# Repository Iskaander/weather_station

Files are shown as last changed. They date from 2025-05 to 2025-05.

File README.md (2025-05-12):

# weather_station

A little weather station I built to go with my spectrometers.

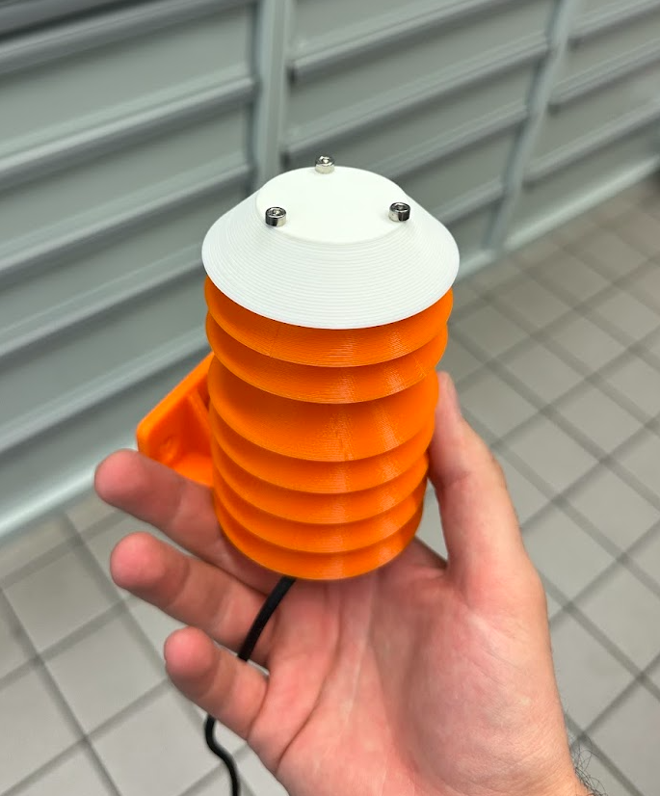
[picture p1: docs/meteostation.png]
The built station

*(The finished weather station setup)*

This is a project for a small, reasonably cheap weather station. The main idea was to have something to measure atmospheric conditions (especially pressure and temperature) when running laser spectrometers. Those readings are complimentary to the measurements of greenhouse gases. But I thought it would be also nice to track humidity and CO2 levels.

I sometimes do the measurements in different places, so I included a GPS receiver. This gives me location, altitude, and time, which I can then use to blend my data with weather models like ERA5.

There are probably off-the-shelf weather stations, but I wanted a specific set of sensors, aiming for good precision for each measurement.
UPD: This is a standard P/T/H station for EU measurements with COCCON: PCE-THB 40 for 300 eur
https://www.pce-instruments.com/deutsch/messtechnik/messgeraete-fuer-alle-parameter/temperatur-datenlogger-temperaturlogger-pce-instruments-temperatur-datenlogger-pce-thb-40-det_3711876.htm

## What's Inside & Cost

Here's the parts list. Total comes out to around $153 USD:

1.  **GPS:** Adafruit ULTIMATE GPS PA1616S - $30
2.  **Pressure:** MIKROE-5921 BMP585 board - $23 (This sensor is new and most precise +-6Pa relative and +-50 Pa absolute accuracy)
3.  **CO2:** Sensirion SCD30 - $33 (Stable NDIR CO2 sensor +-30.0 ppm)
4.  **Temp/Humidity:** Sensirion SHT85 - $28 (Sensirion is known for good accuracy 1.5	%RH accruacy and 0.1 degC for temperature)
5.  **MCU:** Teensy 4.1 - $39 (Versatile and fast up to 600mhz)

An SD card isn't strictly necessary, but if you want to log data, a 16GB one formatted to FAT32 works fine.

## Putting it Together

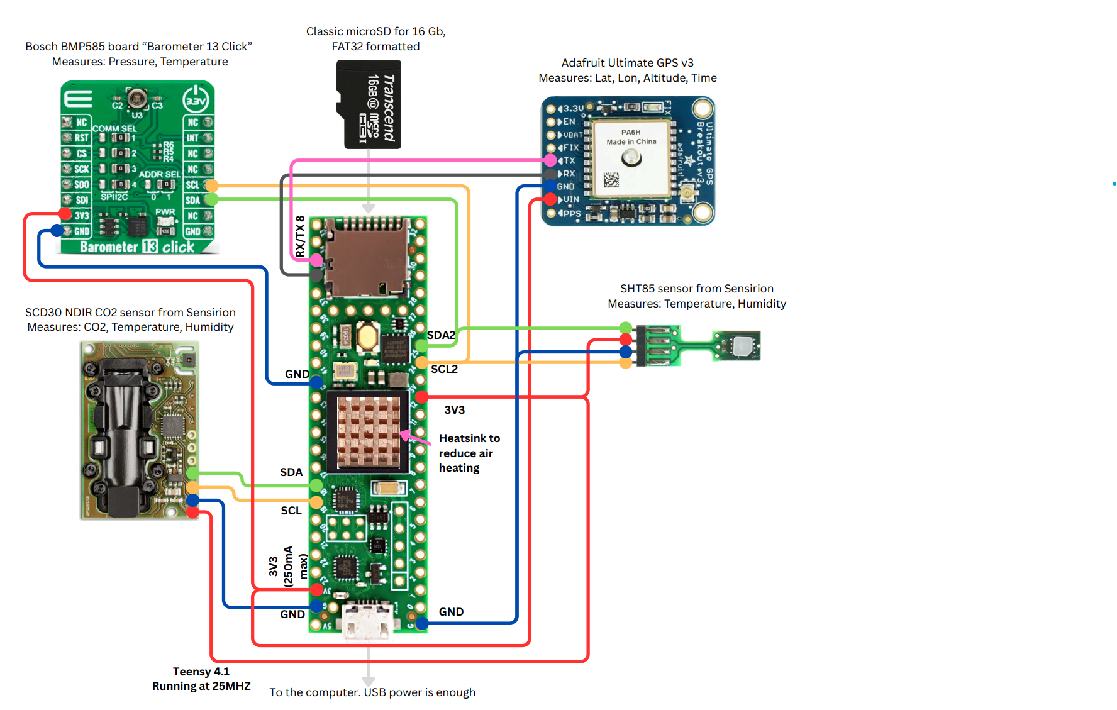
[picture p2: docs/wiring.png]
Wiring diagram

*(How things are wired up)*

I just soldered everything onto a perfboard. No PCB design for this one, as I didn't have the time, and perfboarding it took about a day of wiring and soldering.

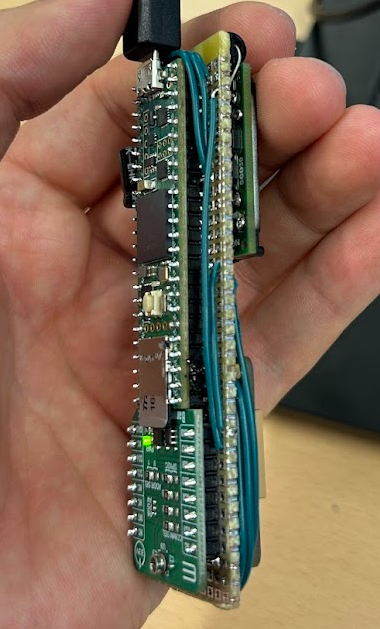
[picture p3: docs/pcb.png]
The PCB

*(The soldered parts)*

Try to put SHT85 sensor away from the heat sources - as this is your precise measurement of air temperature.

The 3D printed enclosure files are great, but you have to stop mid print to insert m3 nuts for the top part. The sensors and Teensy fit nicely. You'll likely need to print 9 of the "middle sections" to get enough height to cover the board properly. You also need m3 rods to connect the parts.

## The Code

 Most of the code was written by Gemini 2.5 Pro Preview (Google). It works... But I am in the middle of my PhD so there is no time for a more readable version.

### Libraries You'll Need:

They are included in the repo, but most of them could be installed via Arudino interface in IDE. Also there was no library for Bosch sensor, so I took parts of the code from this website https://www.electroniclinic.com/bosch-bmp585-barometric-pressure-sensor-with-arduino/

### Getting it Running:
1.  Make sure you have the Arduino IDE and Teens set up.
2.  Install the libraries listed above.
3.  Grab the code from this repository.
4.  Open the main `.ino` file, select Teensy 4.1 as your board, and upload. I also recommend setting teensy CPU speed to 24Mhz in "tools" menu but this is already done.

## How it Works (Briefly)

It checks for SD card, communicates to the sensors and then starts logging data and sending it to the UART. Logging interval is 1 second. After 12hours of logging it will make a new CSV on SD card. If something goes wrong the main LED will turn on. You can also monitor the status via serial interface in arduino. 

This is the CSV header:
"Log_Index,CPU_TempC,BMP_TempC,BMP_PressPa,CO2_ppm,SCD30_TempC,SCD30_Hum_%,SHT_TempC,SHT_Hum_%,GPS_Lat,GPS_Lon,GPS_Alt_m,GPS_Year,GPS_Month,GPS_Day,GPS_Hour,GPS_Min,GPS_Sec,GPS_MilliSec,GPS_Fix,BMP_Health,SCD30_Health,SHT_Health"

Field Descriptions:

- **Log_Index**: For-loop cycle count.
- **CPU_TempC**: Temperature of the Teensy core in °C.
- **BMP_TempC**: Temperature from the BMP585 sensor in °C.
- **BMP_PressPa**: Pressure from the BMP585 sensor in Pascals (Pa).
- **CO2_ppm**: CO2 concentration in ppm from the SCD30 sensor.
- **SCD30_TempC**: Temperature from the SCD30 sensor in °C.
- **SCD30_Hum_%**: Humidity from the SCD30 sensor in %.
- **SHT_TempC**: Temperature from the SHT85 sensor in °C (most precise air temperature).
- **SHT_Hum_%**: Humidity from the SHT85 sensor in % (most precise air humidity).
- **GPS_Lat**, **GPS_Lon**: Coordinates in decimal degrees.
- **GPS_Alt_m**: Altitude above sea level in meters.
- **GPS_Year**, **GPS_Month**, **GPS_Day**, **GPS_Hour**, **GPS_Min**, **GPS_Sec**: Time from GPS.
- **GPS_MilliSec**: Milliseconds from GPS (currently always 0).
- **GPS_Fix**: 1 if GPS has a fix, 0 otherwise.
- **BMP_Health**: 1 if BMP585 is healthy, 0 otherwise.
- **SCD30_Health**: 1 if SCD30 is healthy, 0 otherwise.
- **SHT_Health**: 1 if SHT85 is healthy, 0 otherwise.

## Some results

Here are measurements for the weekend

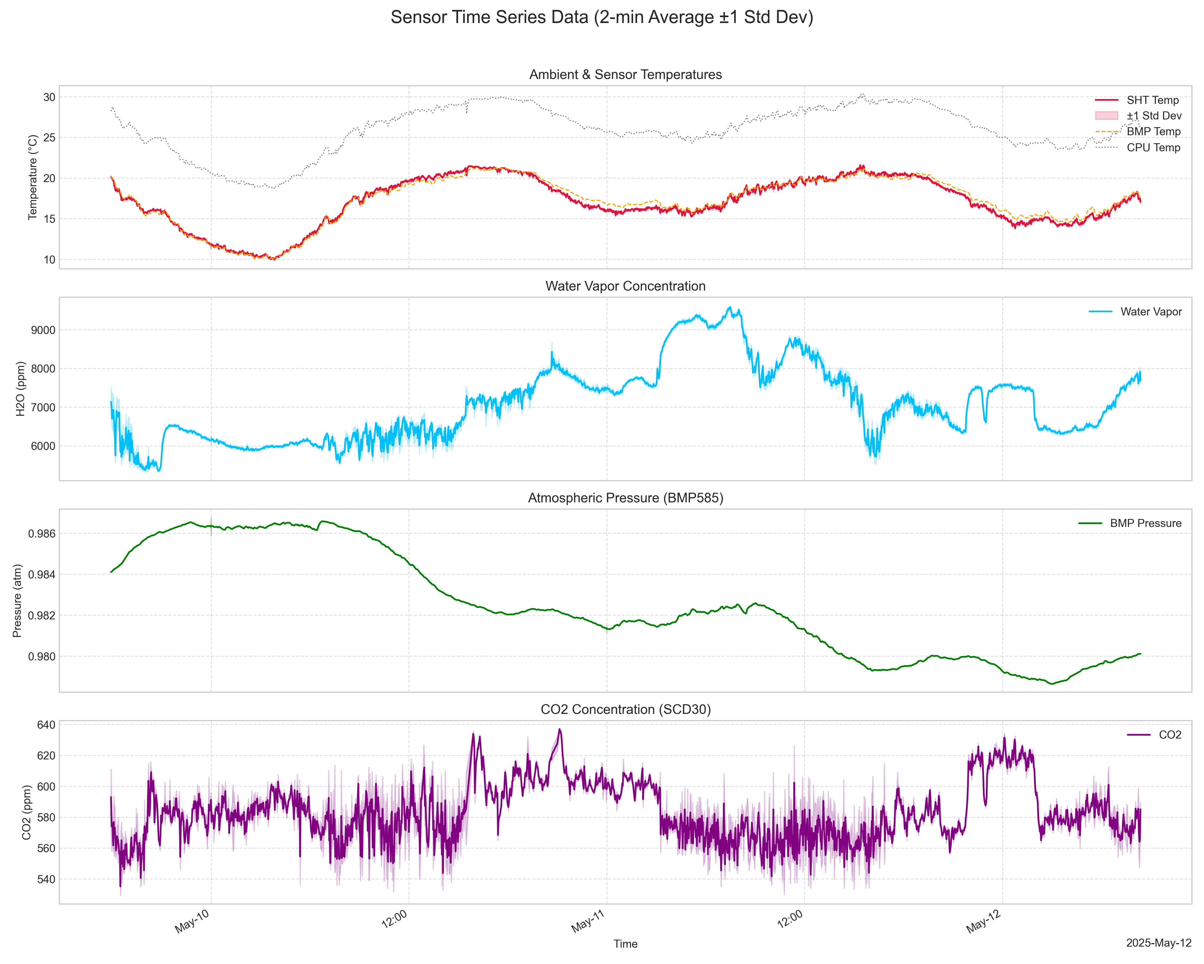
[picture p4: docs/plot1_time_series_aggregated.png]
2 day measurements

*(Measurements during 2 days in the shade in the city)*

And here is a comparison between different sensors

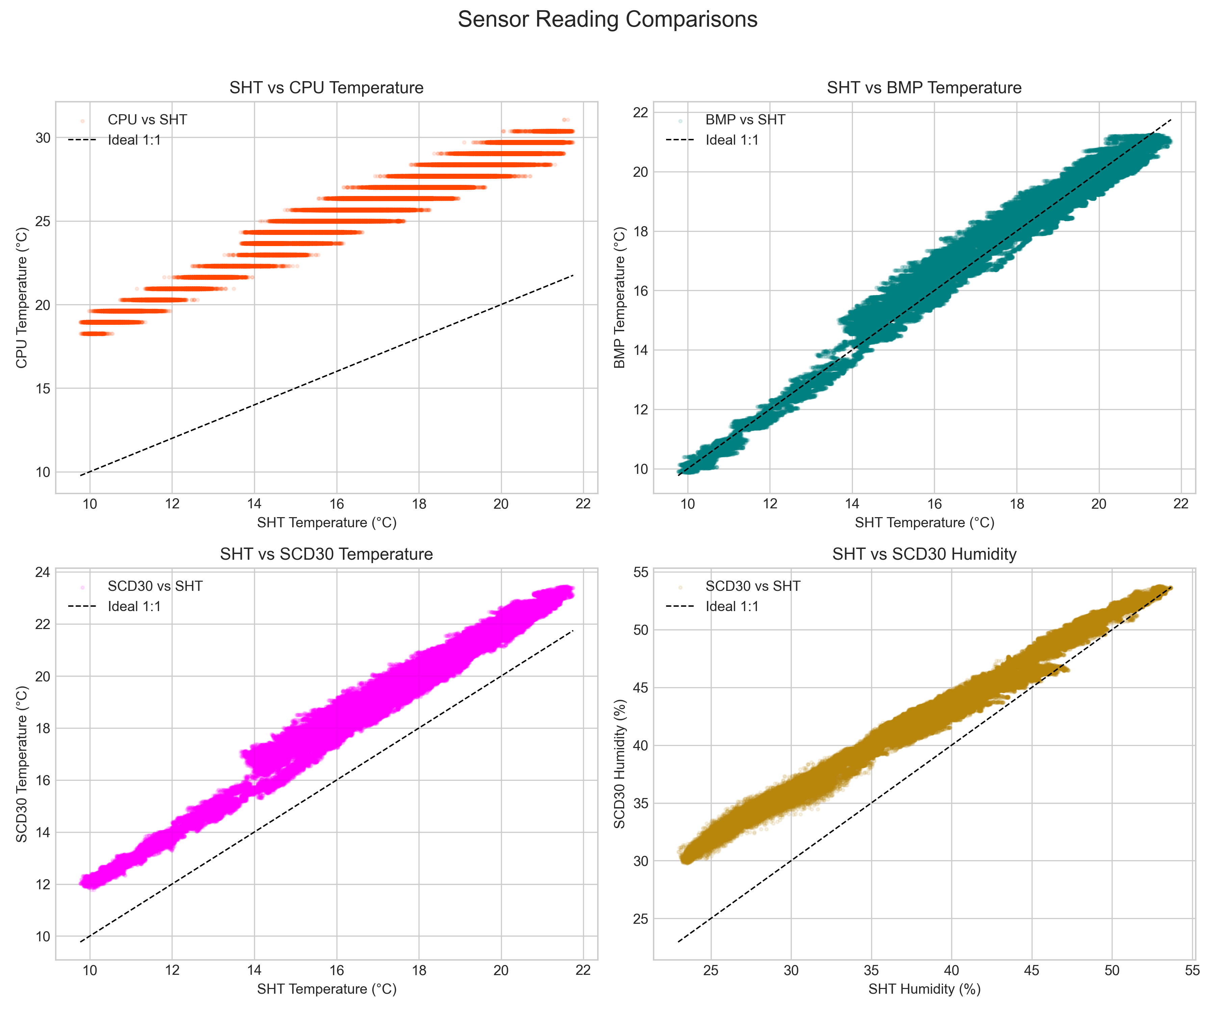
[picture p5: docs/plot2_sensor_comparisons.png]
Comparison

*(cross-comparison between sensors on the weather station)*

## Future tasks

1. Write visualisation from csv in Python
2. Write visualisation in real time in LabView
3. Write SD reading directly from Arduino
4. Fix GPS_MilliSec always = 0
5. Add MTP support to copy files from SD card directly

## Licensing

The code in this project is licensed under the MIT License - see the `LICENSE` file for details.

1.  **3D models:**
    *   The 3D models included in the `/3d_models` directory are licensed under the (CC BY 4.0).
    *   Source: https://www.printables.com/model/73421-radiation-shields-for-diy-weather-station
2.  **Adafruit GPS Library:**
    *   Licensed under the [BSD 3-Clause License]. The full license text is included with the library files.
    *   Source: https://github.com/adafruit/Adafruit_GPS?tab=License-1-ov-file#readme
3.  **Arduino-sht Library:**
    *   Licensed under the [BSD 3-Clause License]. The full license text is included with the library files.
    *   Source: https://github.com/Sensirion/arduino-sht?tab=BSD-3-Clause-1-ov-file#readme
4.  **InternalTemperature Library:**
    *   No license was provided in the repository at the time of creation of this document
    *   Source: https://github.com/LAtimes2/InternalTemperature
5.  **SD Library:**
    *   Licensed under the [GNU GENERAL PUBLIC LICENSE]. The full license text is included with the library files.
    *   Source: https://github.com/arduino-libraries/SD?tab=GPL-3.0-1-ov-file#readme
6.  **SparkFun_BMP581_Arduino_Library Library:**
    *   Licensed under the [MIT License]. The full license text is included with the library files.
    *   Source: https://github.com/sparkfun/SparkFun_BMP581_Arduino_Library?tab=License-1-ov-file#readme
7.  **SparkFun_SCD30_Arduino_Library Library:**
    *   Licensed under the [MIT License]. The full license text is included with the library files.
    *   Source: https://github.com/sparkfun/SparkFun_SCD30_Arduino_Library?tab=License-1-ov-file#readme
8.  **WDT_T4 Library:**
    *   Licensed under the [MIT License]. The full license text is included with the library files.
    *   Source: https://github.com/tonton81/WDT_T4?tab=MIT-1-ov-file#readme
9.  **BMP585 code:**
    *   No License was visible on that page at the time of writing this document
    *   Source: https://www.electroniclinic.com/bosch-bmp585-barometric-pressure-sensor-with-arduino/

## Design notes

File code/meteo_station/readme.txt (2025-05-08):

1. Set teensy CPU clock speed to 150 MHz in Arduino IDE "Tools" section.

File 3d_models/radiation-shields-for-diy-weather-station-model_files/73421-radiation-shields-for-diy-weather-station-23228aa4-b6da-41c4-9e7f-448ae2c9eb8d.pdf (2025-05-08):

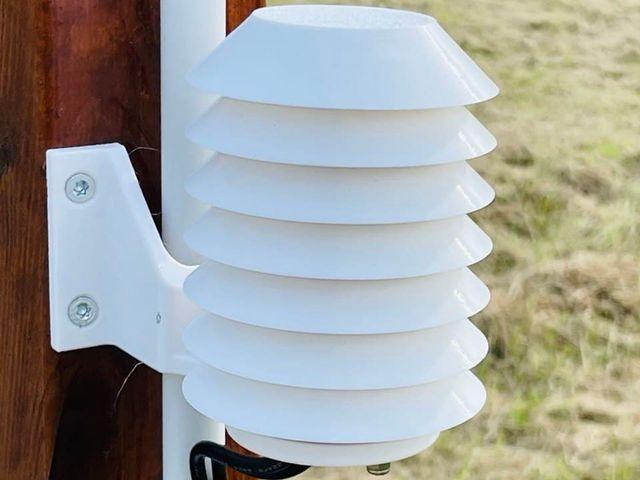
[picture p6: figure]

5.50 hrs

4 pcs

f

0.20 mm

k

0.40 mm

h

PET

51 g

d

Prusa MINI /

MINI+

## Summary

Universal radiation shields for various environmental sensors such as

temperature, air pressure or humidity

Hobby & Makers (https://www.printables.com/model?categoryId=48) | > | Other Ideas (https://www.printables.com/model?categoryId=82)

A universal radiation shield for various environmental sensors such as

temperature, air pressure or humidity. It is recommended to print the

radiation shield from PETG or another UV stable material.

## Print instructions

Parts

2x Stainless Steel Threaded Rod - 250mm M3 (https://s.click.aliexpress.com/e/_A2AYts)

3x Stainless Steel Washer - M3 (https://s.click.aliexpress.com/e/_9G1K2u)

6x Stainless Steel Hexagon Nuts - M3 (https://s.click.aliexpress.com/e/_AZAjvM) foorschtbar (https://www.printables.com/social/97471/about)

## Radiation shields

## for DIY weather

## station

VIEW IN BROWSER (https://www.printables.com/model/73421-radiation-shields-for-diy-weather-station)

updated 13. 9. 2022 | published 13. 9. 2022

•

•

•

# Model files

Assembly

Print one of the Bases (Normal, V2 or V3)

Print Top

Use 4 vertical perimeters

Pause while printing to insert nuts

Print Rings depending on your needs

Use 4 vertical perimeters

I printed six rings

Cut the threaded rods to your needs. Some tips:

The top hole is 6.8mm deep

Each ring needs 12mm

The base needs 12.5mm

Add some space at the end for the nuts and the washer

With six rings I shortened the threaded rods to 100mm

## Links

The links to AliExpress are advertising links. I would be happy if you use

this link, but of course you don't have to. I have linked exactly the offers

from which I have also bought and was satisfied with the supplier and the

goods. The products can of course be bought anywhere.

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
radiation_shield_base.stl

radiation_shield_top.stl

radiation_shield_ring.stl

radiation_shield_auxholder_v3-2.stl

## Print files

h PET | k 0.40 mm | f 0.20 mm | 0.89 hrs | 8 g | d Prusa MINI / MINI+
- Single Ring
h PET | k 0.40 mm | f 0.20 mm | 2.65 hrs | 26 g | d Prusa MINI / MINI+
- Three rings at once
h PET | k 0.40 mm | f 0.20 mm | 1.18 hrs | 12 g | d Prusa MINI / MINI+
h PET | k 0.40 mm | f 0.20 mm | 3.43 hrs | 31 g | d Prusa MINI / MINI+

radiation_shield_auxholder_v3-1.stl

radiation_shield_base_v2.stl

radiation_shield_base_v3-2.stl

radiation_shield_base_v3-1.stl

prusa_radiation_shield_ring_02mm_petg_mini_53m.gcode

prusa_radiation_shield_ring_02mm_petg_mini_2h39.gcode

prusa_radiation_shield_top_02mm_petg_mini_1h11m.gcode

prusa_radiation_shield_base_02mm_petg_mini_3h26.gcode

## License

This work is licensed under a

Creative Commons (4.0 International License)

Attribution (http://creativecommons.org/licenses/by/4.0/)

✖ | Sharing without ATTRIBUTION
✔ | Remix Culture allowed
✔ | Commercial Use
✔ | Free Cultural Works
✔ | Meets Open Definition

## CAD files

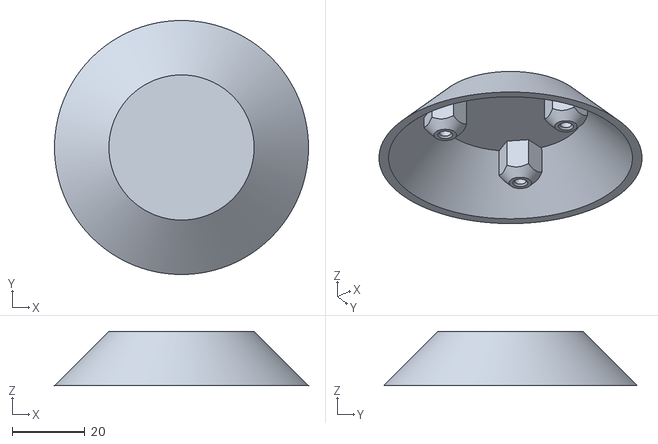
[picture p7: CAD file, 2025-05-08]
3d_models/radiation-shields-for-diy-weather-station-model_files/Radiation_Shield_Top.stl
70.0 x 70.0 x 15.0

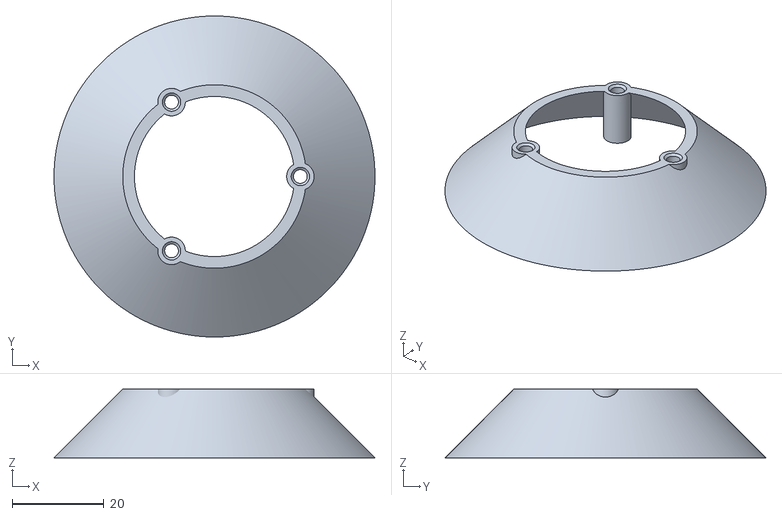
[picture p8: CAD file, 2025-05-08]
3d_models/radiation-shields-for-diy-weather-station-model_files/Radiation_Shield_Ring.stl
70.0 x 70.0 x 15.0

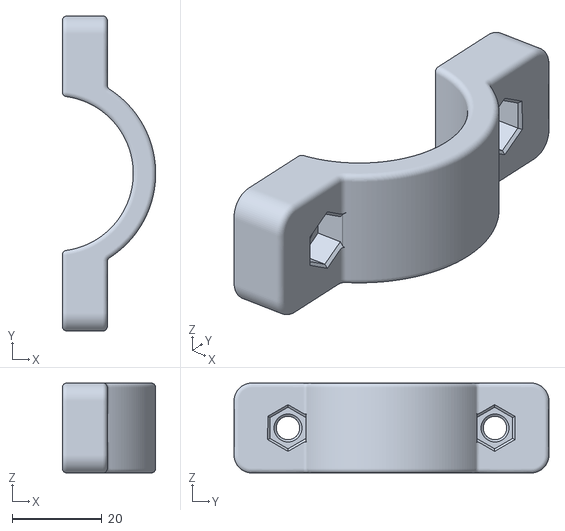
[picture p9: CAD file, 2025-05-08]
3d_models/radiation-shields-for-diy-weather-station-model_files/Radiation_Shield_AuxHolder_v3-2.stl
20.7 x 70.0 x 20.0

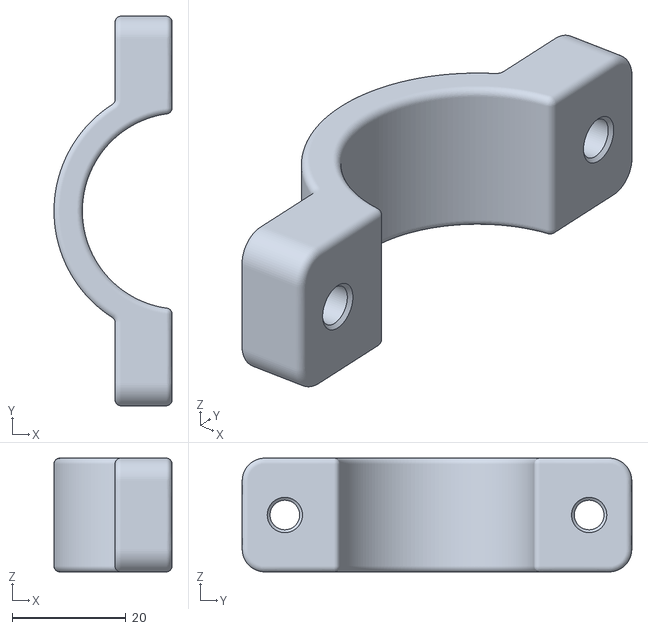
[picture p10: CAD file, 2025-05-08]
3d_models/radiation-shields-for-diy-weather-station-model_files/Radiation_Shield_Base_v3-2.stl
20.7 x 68.5 x 20.0

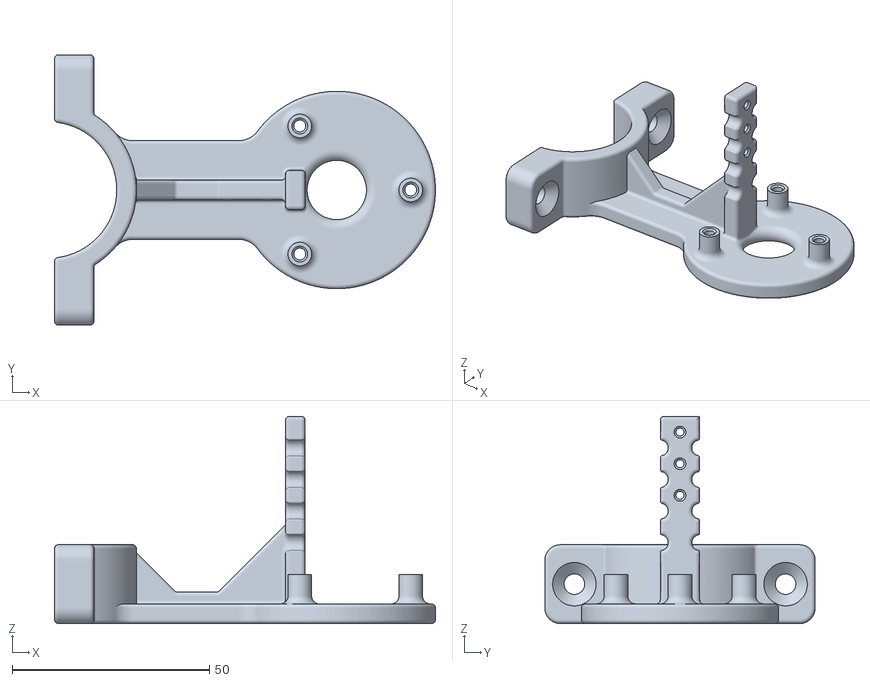
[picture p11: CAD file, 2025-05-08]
3d_models/radiation-shields-for-diy-weather-station-model_files/Radiation_Shield_Base_v3-1.stl
96.5 x 68.5 x 52.5

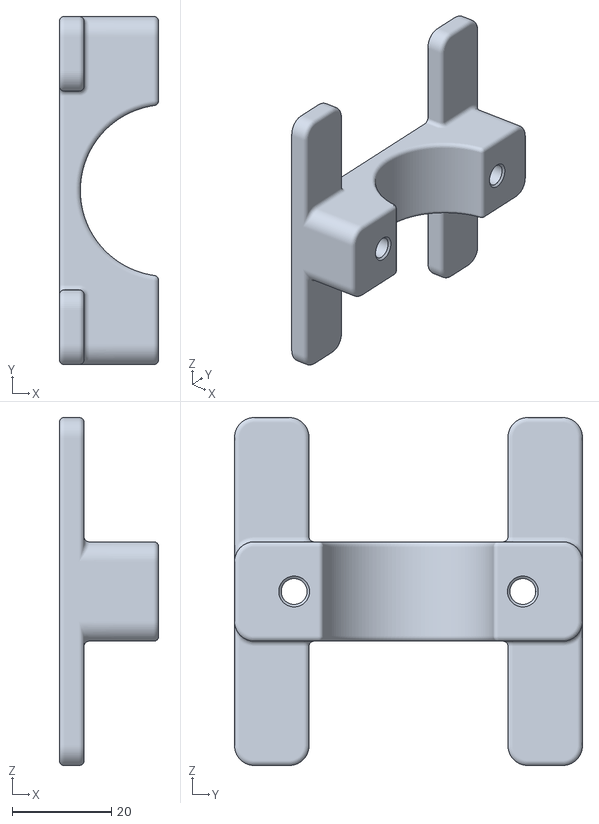
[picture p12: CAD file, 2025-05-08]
3d_models/radiation-shields-for-diy-weather-station-model_files/Radiation_Shield_AuxHolder_v3-1.stl
20.0 x 70.0 x 70.0

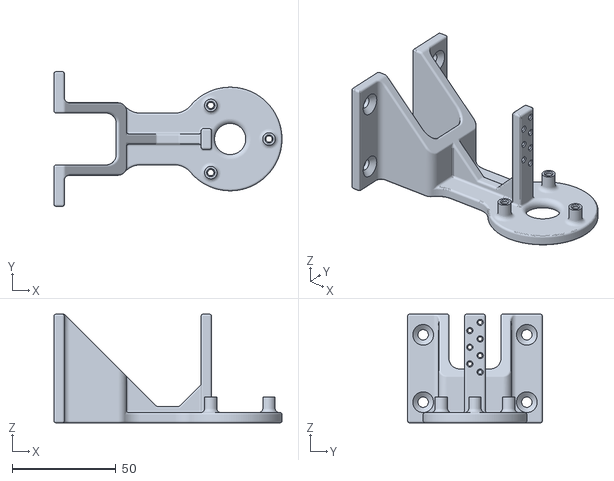
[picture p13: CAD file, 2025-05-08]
3d_models/radiation-shields-for-diy-weather-station-model_files/Radiation_Shield_Base.stl
110.0 x 65.0 x 52.5

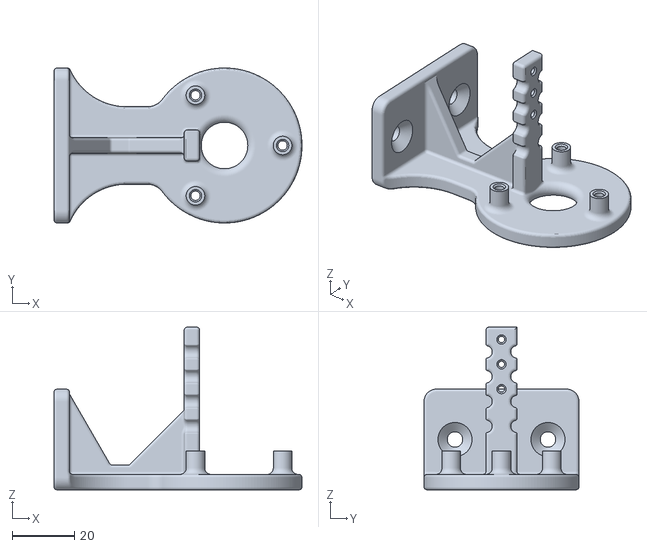
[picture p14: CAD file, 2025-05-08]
3d_models/radiation-shields-for-diy-weather-station-model_files/Radiation_Shield_Base_v2.stl
80.0 x 50.0 x 52.5

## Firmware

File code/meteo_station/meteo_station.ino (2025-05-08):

#include <Wire.h>
#include "SparkFun_BMP581_Arduino_Library.h" // BMP581 library
#include "SparkFun_SCD30_Arduino_Library.h"  // SCD30 library
#include "SHTSensor.h"                      // SHT3x library
#include <SD.h>
#include <SPI.h>
#include <Adafruit_GPS.h>                   // GPS library
#include <Watchdog_t4.h>                    // Watchdog library
#include <InternalTemperature.h>            // Teensy Internal Temp

// --- Watchdog Configuration ---
WDT_T4<WDT1> wdt; 
const int WATCHDOG_TIMEOUT_SECONDS = 20; // Timeout in seconds.

// Sensor objects
SCD30 airSensor;
BMP581 pressureSensor; 
SHTSensor sht1(SHTSensor::SHT3X);

// GPS Configuration
#define GPSSerial Serial8
Adafruit_GPS GPS(&GPSSerial);
#define GPSECHO false
// I2C Address for BMP581
#define I2C_ADDRESS_1 0x46 // BMP581 I2C address
// SD Card Chip Select
const int chipSelect = BUILTIN_SDCARD; // BUILTIN_SDCARD for Teensy 4.1

// --- Global variables to store the last known sensor values ---
float cpu_temp = 0.0;
float lastBmpTemp = 0.0;
float lastBmpPressure = 0.0; // In Pascals (Pa)
int   lastCo2 = 0;
float lastCo2Temp = 0.0;
float lastCo2Humidity = 0.0;
float lastShtTemp = 0.0;
float lastShtHumidity = 0.0;
float lastGpsLat = 0.0;
float lastGpsLon = 0.0;
float lastGpsAlt = 0.0;
uint16_t lastGpsYear = 0;
uint8_t  lastGpsMonth = 0;
uint8_t  lastGpsDay = 0;
uint8_t  lastGpsHour = 0;
uint8_t  lastGpsMinute = 0;
uint8_t  lastGpsSecond = 0;
uint16_t lastGpsMilliSecond = 0;
bool gpsFixAvailable = false;

// --- Global counter for log entries ---
unsigned long logEntryCounter = 0;

// --- SD Card Logging Configuration ---
const unsigned long MAX_DATA_LINES_PER_FILE = 43200; // Approx 12 hours of data at 1 line/sec
unsigned long currentDataLinesInFile = 0;     // Tracks lines in the current file
int currentLogFileNumber = 1;                 // Current log file number, e.g., 1 for LOG_1.TXT
char currentLogFileName[20];                  // Stores the current log file name
const char* CSV_HEADER = "Log_Index,CPU_TempC,BMP_TempC,BMP_PressPa,CO2_ppm,SCD30_TempC,SCD30_Hum_%,SHT_TempC,SHT_Hum_%,GPS_Lat,GPS_Lon,GPS_Alt_m,GPS_Year,GPS_Month,GPS_Day,GPS_Hour,GPS_Min,GPS_Sec,GPS_MilliSec,GPS_Fix,BMP_Health,SCD30_Health,SHT_Health";

// --- Error Handling and LED ---
bool mainLedTurnedOnError = false; // Tracks if the main LED has been turned on due to an error

// --- Sensor Health Tracking ---
unsigned long lastBmpSuccessTime = 0;
unsigned long lastScd30SuccessTime = 0;
unsigned long lastShtSuccessTime = 0;
// Timeout durations for sensors (in milliseconds)
const unsigned long SENSOR_TIMEOUT_MS_BMP_SHT = 20000; // 20 seconds
const unsigned long SENSOR_TIMEOUT_MS_SCD30 = 20000; // 20 seconds for SCD30

// --- Sensor Health Flags (will be logged) ---
bool bmpHealthOk = false;
bool scd30HealthOk = false;
bool shtHealthOk = false;

// --- START OF MODIFICATIONS: Global variables for pressure averaging ---
const int PRESSURE_AVG_WINDOW_SIZE = 60;
float pressureValuesForAvg[PRESSURE_AVG_WINDOW_SIZE];
int pressureValueCount = 0;
// --- END OF MODIFICATIONS: Global variables ---


// --- Function to turn on the main LED ---
void turnOnMainLed() {
    digitalWrite(LED_BUILTIN, HIGH);
    if (!mainLedTurnedOnError) {
        Serial.println("CRITICAL ERROR DETECTED: Main LED has been turned ON. Please check system.");
        mainLedTurnedOnError = true;
    }
}

void setup() {
    pinMode(LED_BUILTIN, OUTPUT);
    digitalWrite(LED_BUILTIN, LOW); // Start with LED OFF

    Serial.begin(115200);
    // while(!Serial && millis() < 4000); // Optional: wait for serial port to connect with timeout
    Serial.println("System Setup Starting...");

    Serial.print("Initializing Watchdog with timeout: ");
    Serial.print(WATCHDOG_TIMEOUT_SECONDS);
    Serial.println(" seconds.");
    WDT_timings_t config;
    config.timeout = WATCHDOG_TIMEOUT_SECONDS; // Set timeout
    config.window = 0; // Window must be 0 for this WDT_T4 version or less than timeout
    wdt.begin(config);
    wdt.feed(); // Feed watchdog

    Serial.println("Initializing SD card...");
    if (!SD.begin(chipSelect)) {
        Serial.println("SD Card failed, or not present. System Halted.");
        turnOnMainLed(); // Turn on LED to indicate critical failure
    } else {
        Serial.println("SD card initialized.");
    }
    
    Serial.println("Determining new log file name...");
    currentLogFileNumber = 1; 
    while (true) {
        sprintf(currentLogFileName, "LOG_%d.TXT", currentLogFileNumber);
        if (SD.exists(currentLogFileName)) {
            currentLogFileNumber++; 
            if (currentLogFileNumber > 999999) { 
                Serial.println("Exceeded maximum log file number search (999999). System Halted.");
                turnOnMainLed();
                // Consider halting if this state is reached
            }
        } else {
            break; 
        }
    }
    currentDataLinesInFile = 0; 
    Serial.print("Will create and write to new log file: ");
    Serial.println(currentLogFileName);

    Wire.begin();  // Main I2C bus
    Wire2.begin(); // Second I2C bus
    delay(100);    // Allow I2C to settle

    Serial.println("Initializing BMP581...");
    if (!pressureSensor.beginI2C(I2C_ADDRESS_1, Wire2)) { 
        Serial.println("SETUP ERROR: BMP581 not detected. Please check wiring.");
        turnOnMainLed();
    } else {
        Serial.println("BMP581 initialized.");
        lastBmpSuccessTime = millis();
        if (lastBmpSuccessTime == 0) lastBmpSuccessTime = 1; 
    }
    delay(100);
    writeRegister(I2C_ADDRESS_1, 0x18, 0b00000011, Wire2); 
    delay(100);
    writeRegister(I2C_ADDRESS_1, 0x31, 0b00111111, Wire2); 
    delay(100);
    writeRegister(I2C_ADDRESS_1, 0x36, 0b01111111, Wire2); 
    delay(100);
    writeRegister(I2C_ADDRESS_1, 0x30, 0b11111011, Wire2); 
    delay(100);
    writeRegister(I2C_ADDRESS_1, 0x37, 0b11110001, Wire2); 
    delay(100);

    Serial.println("Initializing SCD30...");
    if (airSensor.begin(Wire) == false){
      Serial.println("SETUP ERROR: Air sensor (SCD30) not detected. Please check wiring.");
      turnOnMainLed();
    } else {
        Serial.println("SCD30 initialized.");
        airSensor.setMeasurementInterval(2); 
        lastScd30SuccessTime = millis();
        if (lastScd30SuccessTime == 0) lastScd30SuccessTime = 1;
    }
    delay(100);

    Serial.println("Initializing SHT3x...");
    sht1.init(Wire2); 
    if (!sht1.readSample()) { 
        Serial.println("SETUP ERROR: SHT3x not detected or error reading sample on setup.");
        turnOnMainLed();
    } else {
        Serial.println("SHT3x initialized and first sample read.");
        lastShtSuccessTime = millis();
        if (lastShtSuccessTime == 0) lastShtSuccessTime = 1;
    }

    GPSSerial.begin(9600);
    GPS.begin(9600); 
    GPS.sendCommand(PMTK_SET_NMEA_OUTPUT_ALLDATA); //PMTK_SET_NMEA_OUTPUT_RMCGGA
    GPS.sendCommand(PMTK_SET_NMEA_UPDATE_1HZ);    
    GPS.sendCommand(PGCMD_ANTENNA);               
    delay(1000); 

    Serial.println("Setup complete. Starting main loop.");
}

unsigned long previousLogTime = 0;
const unsigned long logInterval = 1000; // Log data every 1 second

void loop() {
    wdt.feed(); 
    unsigned long currentMillis = millis();

    while (GPSSerial.available() > 0) { 
        GPS.read();
    }

    if (GPS.newNMEAreceived()) {
        if (GPS.parse(GPS.lastNMEA())) { 
            if (GPS.fix) {
                gpsFixAvailable = true;
                lastGpsLat = GPS.latitudeDegrees;
                lastGpsLon = GPS.longitudeDegrees;
                lastGpsAlt = GPS.altitude;
                lastGpsYear = GPS.year + 2000; 
                lastGpsMonth = GPS.month;
                lastGpsDay = GPS.day;
                lastGpsHour = GPS.hour;
                lastGpsMinute = GPS.minute;
                lastGpsSecond = GPS.seconds;
                lastGpsMilliSecond = GPS.milliseconds;
            } else {
                gpsFixAvailable = false;
            }
        }
    }

    bmp5_sensor_data bmpData = {0, 0}; 
    int8_t bmpErr = pressureSensor.getSensorData(&bmpData);
    if (bmpErr == BMP5_OK) {
        lastBmpTemp = bmpData.temperature; 
        uint32_t rawPressure = readPressure(Wire2); 
        lastBmpPressure = convertRawPressure(rawPressure); 
        lastBmpSuccessTime = currentMillis; 

        // --- Averaging pressure for SCD30 offset ---
        // Check if the converted pressure is valid (e.g., greater than 0 Pa).
        // BMP5_OK ensures sensor data is valid; convertRawPressure might return 0 if its internal read failed.
        if (lastBmpPressure > 0) { 
            pressureValuesForAvg[pressureValueCount] = lastBmpPressure;
            pressureValueCount++;

            if (pressureValueCount >= PRESSURE_AVG_WINDOW_SIZE) {
                float sumOfPressures = 0.0;
                for (int i = 0; i < PRESSURE_AVG_WINDOW_SIZE; i++) {
                    sumOfPressures += pressureValuesForAvg[i];
                }
                float averagePressurePa = sumOfPressures / PRESSURE_AVG_WINDOW_SIZE;
                uint16_t averagePressureMbar = (uint16_t)(averagePressurePa / 100.0); // Convert Pa to mbar

                //Serial.print("Collected 60 pressure samples. Average (Pa): "); Serial.print(averagePressurePa);
                //Serial.print(" -> mbar for SCD30: "); Serial.println(averagePressureMbar);

                if (airSensor.setAmbientPressure(averagePressureMbar)) {
                    //Serial.println("SCD30: Ambient pressure compensation successfully set.");
                } else {
                    Serial.println("SCD30: FAILED to set ambient pressure compensation.");
                }
                
                pressureValueCount = 0; // Reset counter for the next averaging window
            }
        }
    } 

    if (airSensor.dataAvailable()) {
        lastCo2 = airSensor.getCO2();
        lastCo2Temp = airSensor.getTemperature();
        lastCo2Humidity = airSensor.getHumidity();
        lastScd30SuccessTime = currentMillis; 
    }

    if (sht1.readSample()) { 
        lastShtTemp = sht1.getTemperature();
        lastShtHumidity = sht1.getHumidity();
        lastShtSuccessTime = currentMillis; 
    } 

    if (lastBmpSuccessTime != 0 && (currentMillis - lastBmpSuccessTime > SENSOR_TIMEOUT_MS_BMP_SHT)) {
        Serial.println("LOOP ERROR: BMP581 has not updated data recently.");
        turnOnMainLed(); 
    }
    if (lastScd30SuccessTime != 0 && (currentMillis - lastScd30SuccessTime > SENSOR_TIMEOUT_MS_SCD30)) {
        Serial.println("LOOP ERROR: SCD30 has not provided data recently.");
        turnOnMainLed(); 
    }
    if (lastShtSuccessTime != 0 && (currentMillis - lastShtSuccessTime > SENSOR_TIMEOUT_MS_BMP_SHT)) {
        Serial.println("LOOP ERROR: SHT3x has not updated data recently.");
        turnOnMainLed(); 
    }

    cpu_temp = InternalTemperature.readTemperatureC();

    if (currentMillis - previousLogTime >= logInterval) {
        previousLogTime = currentMillis;

        bmpHealthOk = (lastBmpSuccessTime != 0) && ((currentMillis - lastBmpSuccessTime) <= SENSOR_TIMEOUT_MS_BMP_SHT);
        scd30HealthOk = (lastScd30SuccessTime != 0) && ((currentMillis - lastScd30SuccessTime) <= SENSOR_TIMEOUT_MS_SCD30);
        shtHealthOk = (lastShtSuccessTime != 0) && ((currentMillis - lastShtSuccessTime) <= SENSOR_TIMEOUT_MS_BMP_SHT);

        if (currentDataLinesInFile >= MAX_DATA_LINES_PER_FILE) {
            currentLogFileNumber++; 
            if (currentLogFileNumber > 999999) { 
                Serial.println("Exceeded maximum log file number (999999) during rollover. System Halted.");
                turnOnMainLed();
            }
            currentDataLinesInFile = 0; 
            sprintf(currentLogFileName, "LOG_%d.TXT", currentLogFileNumber);
            Serial.print("Max data lines reached. Rolling over to new log file: ");
            Serial.println(currentLogFileName);
        }
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
